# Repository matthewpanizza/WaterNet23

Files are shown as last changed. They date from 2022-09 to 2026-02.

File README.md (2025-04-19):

# WaterNet23 - Autonomous Water Vehicles
Repository for WaterNet23 Code and Schematics

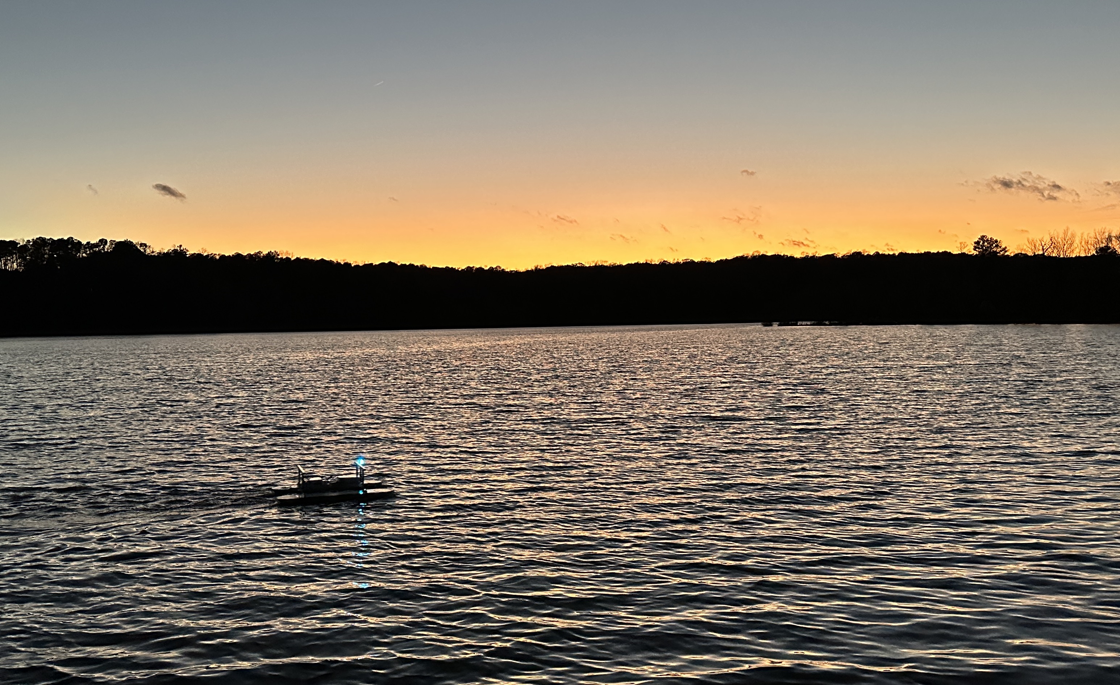
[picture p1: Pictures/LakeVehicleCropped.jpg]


## Background

This project was started as part of the one-year NC State ECE Senior Design class in January 2022. The goal of this project was to develop a series of low-cost autonomous water surface vehicles which could collect water quality measurements of aquaculture ponds. This README contains information on how to set up the water vehicles for operation and details on the hardware and software used for the project.

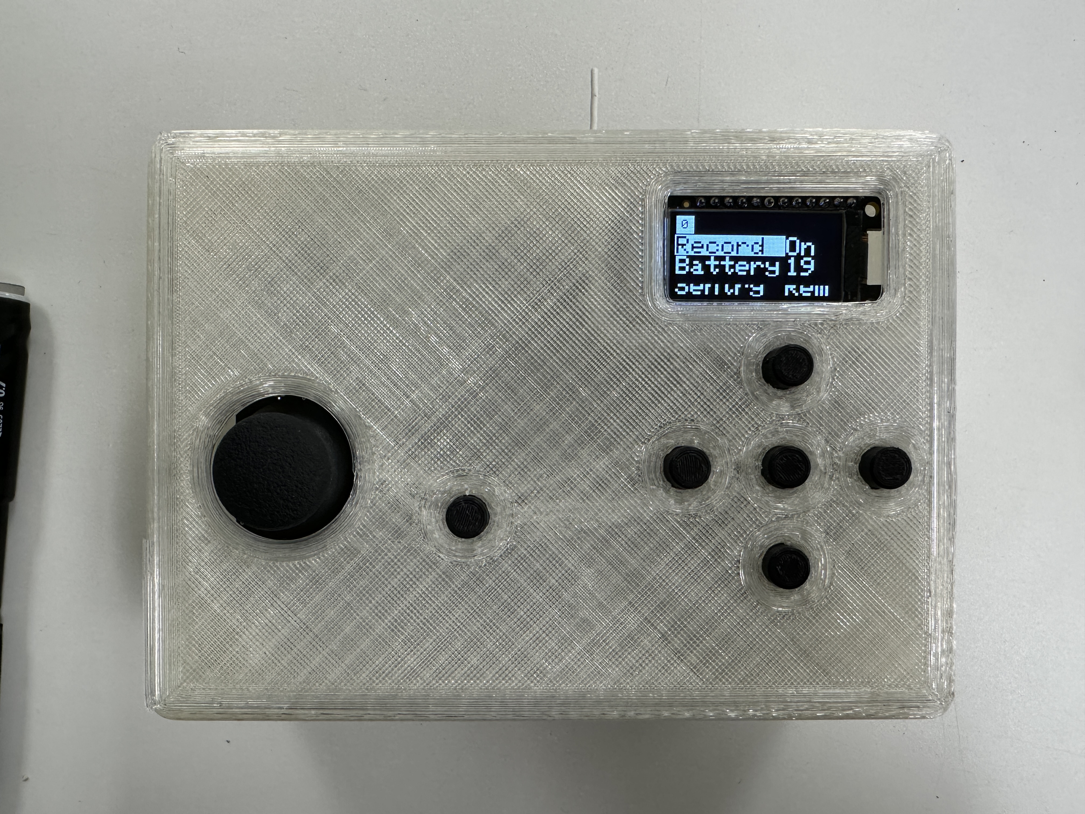
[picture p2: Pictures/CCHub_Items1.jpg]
 

This project has two parts - the water vehicles and the Central Control Hub (CCHub). The CCHub communicates wirelessly with the vehicles using XBee (900MHz), Cellular (LTE) and Bluetooth Low Energy (BLE) with support for up to 10 vehicles. The water vehicles report telemetry back to the CCHub, which is then displayed on the CCHub's screen. The vehicles have three operation modes for movement: remote control, sentry and autonomous. Remote control allows for control using the CCHub joystick. Sentry mode captures the current GPS location and attempts to keep the vehicle within a set radius of that point. Autonomous mode allows for navigation to GPS waypoints which are fed into the CCHub over Serial from a companion computer. See the [Operating the Water Vehicles](#operating-the-water-vehicles) section for more information on how these functions work.

## Table of Contents
 - **[Features](#features)**: Hardware/software capabilities of the vehicles and CCHub.
 - **[Operating the Water Vehicles](#operating-the-water-vehicles)**: How to use the CCHub to control the water vehicles.
 - **[Hardware](#hardware)**: Information about the hardware components used on the CCHub and vehicles.
 - **[Software](#software)**: Information about the software communication and control systems.
 - **[Setting Up the Development Environment](#setting-up-the-development-environment)**: Information about hwo to install Visual Studio Code and upload code to the microcontrollers.
 - **[Software Architecture](#software-architecture)**: Information about common software practices used in the programming of the boards and quick links to get you started on understanding the microcontroller functions.

## Features
 - Network support for controlling up to 10 water vehicles
 - Autonomous navigation mode for movement to GPS waypoints
 - Sentry mode to maintain position for continuous measuring in one place
 - Graphical menu for configuring vehicles and observing status
 - Redundant communication via LTE, XBee and Bluetooth LE
 - Water quality sensing for temperature, dissolved oxygen, pH, and conductivity
 - Logging of water quality measurements on a micro-SD card
 - Wireless copying of water quality measurements from vehicles to CCHub micro-SD card
 - 80W solar panel for long-term stationary monitoring
 - Light tower for observing vehicle status from shoreline
 - Leak detection emergency shutoff

## Operating the Water Vehicles

This section has instructions for powering up the water vehicles and operating them using the Central Control Hub.

### Powering the CCHub and Water Vehicles

The CCHub has a micro USB port on its side which needs to be powered with a high-amperage (2.1A) USB brick or power bank. Once plugged in, the CCHub will automatically attempt to establish Cellular connection and receive messages from the water vehicles.

The water vehicles are powered from the a Lithium-ion battery pack and have a button for powering up the board. There is a latching mechanism on the main board which will keep the power on once the microcontroller has started operating. Hold the power button for five seconds to ensure the power latch is enabled. Like the CCHub, the water vehicles will attempt to establish a Cellular connection and will broadcast periodic messages for the CCHub to pick up.

Once a vehicle has connected to cellular and the CCHub has received the message, it will show up on the CCHub screen as a block with its identifier ID. See the next section for how to navigate the menu on the CCHub.

### Menu Navigation

The CCHub menu is navigated using the integrated DPAD buttons. When not modifying a setting, the left/right buttons switch which vehicle is being controlled, and the up/down arrows navigate which item is being selected. To modify one of the settings, press the enter button and it will highlight the value to be changed. Use the left/right buttons to modify the value and press enter to confirm. There is also an emergency stop toggle next to the joystick which will stop motion of all vehicles.

#### Settings
- **Record**: Enables/Disables logging of water quality measurements to the SD card (on/off)
- **Battery**: Estimated battery percentage of the water vehicle's battery (not editable)
- **Sentry**: The current [Driving Mode](#driving-modes) of this water vehicle (Rem/Sen/Aut)
- **Signal**: Turning on signal causes the light tower of this vehicle to flash amber (on/off)
- **SolPwr**: Shows how many watts the solar panel is generating (not editable)
- **BatPwr**: Shows how many watts are being drawn from the Lithium-ion battery (not editable)
- **Offload**: Starts a copy of all files from the vehicles microSD card to the CCHub microSD card over Bluetooth. Only enable when vehicles are docked! (on/off)

### Driving Modes

#### Remote Control (Rem)

Remote control mode allows the user to use the joystick on the CCHub to control the direction and speed of the vehicle manually like an RC car. In remote mode, the joystick controls whichever vehicle is currently selected on the menu.

#### Sentry (Sen)

Changing the control mode to Sentry mode will send a target latitude and longitude waypoint to the vehicle and have the vehicle navigate to that point. After it reaches that point, it will use the GPS and compass to navigate back to that target point if it goes farther than a set radius (current software is set to 4 meters). This mode can be used to take samples of one part of a water body over a large period of time, as it will correct for water currents pushing the vehicle.

#### Autonomous (Aut)

Changing the control mode to autonomous mode will send a target latitude and longitude waypoint to the vehicle and have the vehicle navigate to that point. These GPS waypoints are fed into the CCHub via the USB port which is connected to companion computer. See the next section for information about the companion computer.

### Companion Computer and Waypoints

The CCHub is set up to be connected over USB to a companion computer such as a Raspberry Pi for automated sending of GPS waypoints. There are a series of commands that can be sent to the CCHub which are then transmitted to the water vehicles. See the [Companion Computer to CCHub Command Structure](#companion-computer-to-cchub-command-structure) section for how to send the GPS waypoints to the CCHub.

### Light Tower Statuses

The water vehicles are equipped with a small light tower that has an RGB LED. The LED will change colors/blinking patterns depending on which mode it is in and which communication protocols are available.

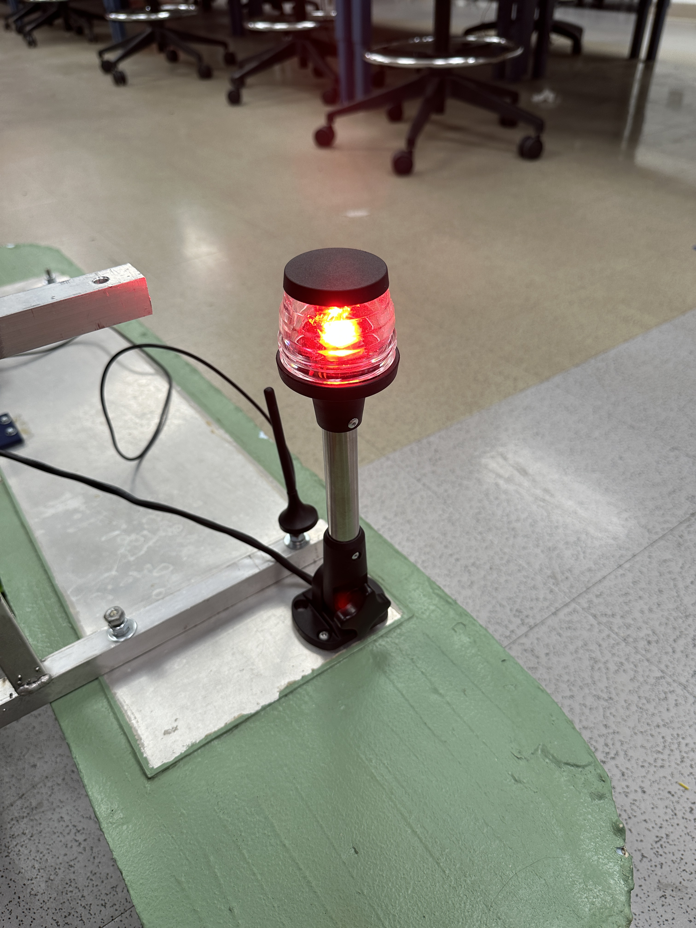
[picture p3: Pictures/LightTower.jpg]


#### Color Schemes
Color     | Description
----------|------------------------------------------
CYAN      | All modes of communication are available
YELLOW    | XBee and BLE are available
WHITE     | LTE and BLE are available
BLUE      | Only BLE available
GREEN     | XBee and LTE available (typical when out in water)
ORANGE    | Only Xbee available
MAGENTA   | Only LTE is available (recovery mode)
RED       | No communication available

#### Blinking Patterns
Pattern            | Description
-------------------|---------------------------
Blinking (normal)  | Battery is low
Blinking (slow)    | Sentry Mode
Fading             | Autonomous Mode
Solid              | Manual Mode

#### Special Modes
Pattern               | Description
----------------------|----------------------------------
Fast Blinking Blue    | Copying micro-SD data to CCHub
Fast Blinking Amber   | Signaling response from CCHub

### Water Quality Sensors
The water vehicles are equipeed with a series of water quality sensors which connect to five SMA connectors on the side of the enclosure. Ensure the sensors are color-matched to the daughter boards on the vehicle PCB. See the [Atlas Scientific Water Quality Sensors](#atlas-scientific-water-quality-sensors) section for how these sensors work and how to configure them on new vehicles.

### Micro-SD Card Logging
Each of the water vehicles have an onboard Micro-SD card reader (on underside of PCB) which is used to store the water quality measurement in a CSV file. This file can be opened in Excel or other sheet processing programs for data analysis of the collected measurements. Below are a few sample measurements on a bench for the temperature and pH probes.

Time           | Latitude | Longitude | Temperature | pH       | Dissolved O2 | Conductivity 0.1K | Conductivity 1K
---------------|----------|-----------|-------------|----------|--------------|-------------------|-----------------
08132022201055 | 0.000000 | 0.000000  | 32.425999   | 3.623000 | 0.000000     | 0.000000          | 0.000000
08132022201057 | 0.000000 | 0.000000  | 32.437000   | 3.616000 | 0.000000     | 0.000000          | 0.000000
08132022201100 | 0.000000 | 0.000000  | 32.438999   | 3.604000 | 0.000000     | 0.000000          | 0.000000
08132022201102 | 0.000000 | 0.000000  | 32.443001   | 3.614000 | 0.000000     | 0.000000          | 0.000000

## Hardware

### Water Vehicle PCB



### Water Vehicle Block Diagram

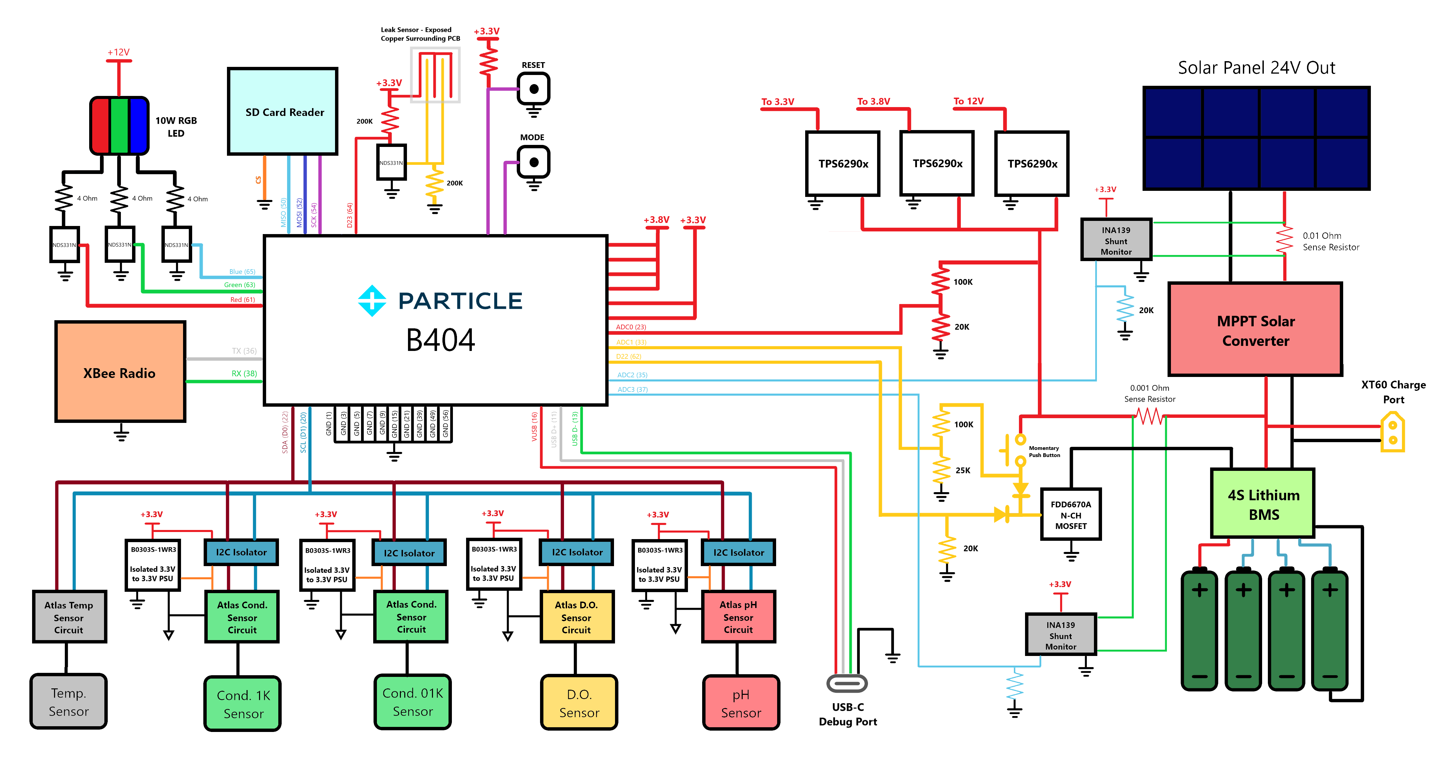
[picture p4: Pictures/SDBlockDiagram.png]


### Particle B402/B404X Microcontroller



For controlling all of the hardware on both the vehicles and CCHub, we used the Particle B-Series System-on-a-Module (BSoM). We chose the BSoMs for their integrated Cellular and Bluetooth Low-Energy communication capability and relatively low cost (~$55/module). These microcontrollers have fairly generous IO and memory capability and are easy to program in C++ using their Particle DeviceOS hardware abstraction layer (HAL). Particle also includes 100MB/month of cellular data in their free plan, which would be plenty for using LTE as a fallback communication mechanism. See the [Software Architecture](#software-architecture) section for more details on how to set up the environment for developing and uploading the firmware on the BSoM.

### Atlas Scientific Water Quality Sensors

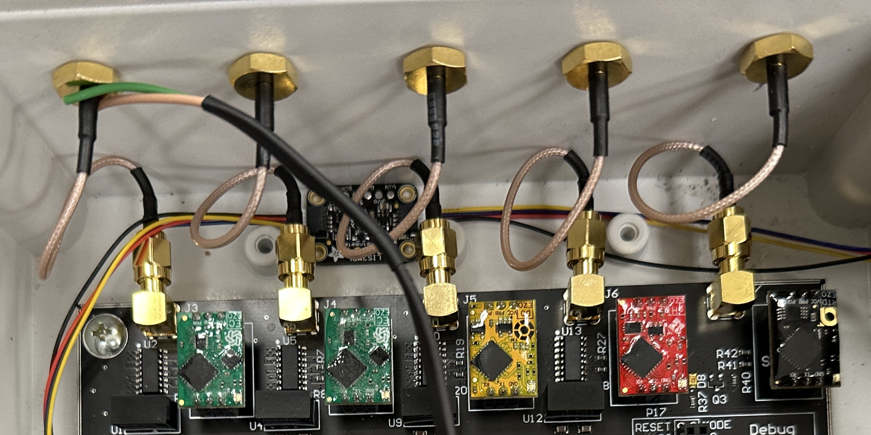
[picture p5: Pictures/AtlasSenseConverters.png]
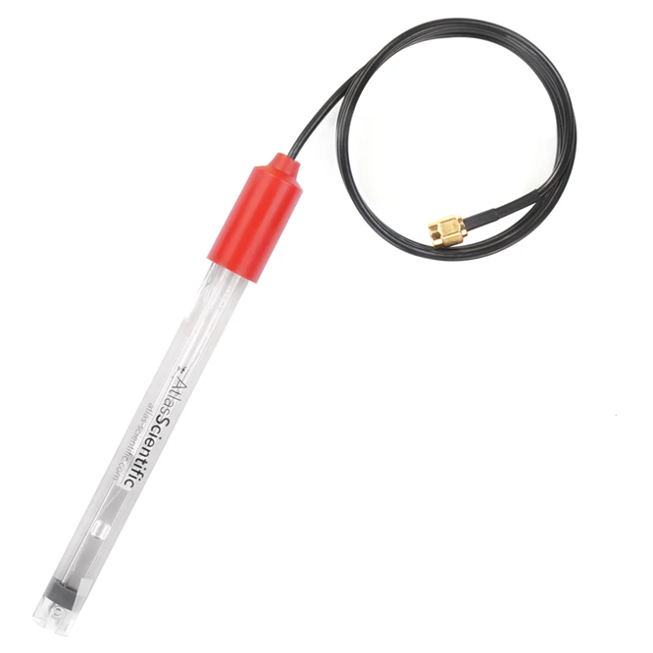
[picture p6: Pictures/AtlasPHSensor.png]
 

The water vehicles have a series of [Atlas Scientific](https://atlas-scientific.com/) water quality sensors. The sensor probes connect using a set of SMA connectors which mount to the exterior of the main PCB enclosure. Ensure the sensors are connected to the SMA connector that matches the circuit (red pH probe goes to the connector in front of the red EZO module). Currently, the vehicle is equipped with the following sensors:

- [Temperature](https://atlas-scientific.com/probes/standard-temp-probe/)
- [pH](https://atlas-scientific.com/probes/consumer-grade-ph-probe/)
- [Dissolved Oxygen](https://atlas-scientific.com/probes/dissolved-oxygen-probe/)
- [Conductivity K 0.1](https://atlas-scientific.com/kits/conductivity-k-0-1-kit/)
- [Conductivity K 1.0](https://atlas-scientific.com/kits/mini-conductivity-k-1-0-kit/)

These sensors use their standard [EZO](https://atlas-scientific.com/embedded-solutions/ezo-ph-circuit/) interface which communicates over I2C to the BSoM microcontroller. Since the interface is standard, the modules/sensors can be swapped out for others that Atlas sells such as the [Oxygen reduction potential](https://atlas-scientific.com/orp) sensor with some slight code modifications.

#### Important Note
The sensors need to be configured to operate in I2C mode with a particular address. By default, they operate in UART mode. See the [pH EZO datasheet](https://files.atlas-scientific.com/pH_EZO_Datasheet.pdf) for the commands needed to switch to I2C mode. You can communicate over UART using a simple USB COM Port adapter (such as FT232RL) or using an Analog Discovery 2. In the software, there are macros which set the I2C address used by each sensor:

```cpp
#define PHADDR              99              //default I2C ID number for EZO pH Circuit.
#define MCOND               100             //default I2C ID number for EZO Mini-Conductivity (0.1)
#define COND                101             //default I2C ID number for EZO Conductivity Circuit. (1.0)
#define TEMPADDR            102             //Default I2C address for temperature sensor
#define DOADDR              97              //Default I2C address for Dissolved Oxygen sensor
```

The I2C system also has a set of I2C isolator circuits which are necessary to prevent interference between the sensors when they make contact with water. Without the isolators, the sensors will feed back into each other and cause inaccurate readings. All EZO circuits, except the temperature probe, have the I2C isolation. The isolation is done using a 3.3V to 3.3V isolated power supply and a I2C isolator IC.

### XBee Radio

In addition to Cellular and BLE, we included a XBee S3B wireless module on the vehicles and CCHub. These modules offer greater range (up to 9 miles!) at similar latency to BLE. The XBee modules we chose operate in the 900MHz range (the same as LoRa), and offer an easy-to-use mesh based communication between all modules in the network. These modules essentially act as a wireless UART console between all nodes in the network, and our command structure handles negotiation of the destination node. Below is an example of communication with XBee between two microcontrollers:

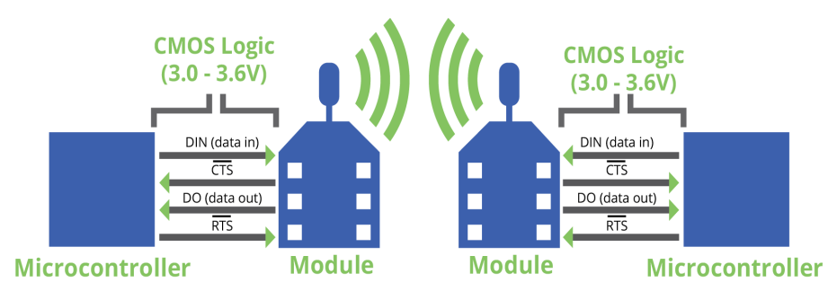
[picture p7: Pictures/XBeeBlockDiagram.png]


**Important Note**: The XBee modules require network setup to become part of a mesh network. Check out this [Instructables setup guide](https://www.instructables.com/How-to-Use-XBee-Modules-As-Transmitter-Receiver-Ar/) for configuring them. For setting up new vehicles, connect the XBee from the CCHub to XCTU and get the channel number. For more information about the XBee S3B Modules, check out the [Datasheet](https://docs.digi.com/resources/documentation/digidocs/pdfs/90002173.pdf).

### Neo-M8U GPS

For autonomous navigation, we decided to use the [Neo-M8U GPS](https://www.sparkfun.com/sparkfun-gps-dead-reckoning-breakout-neo-m8u-qwiic.html) for its accuracy at low cost. This module also has the convenience of the [QWIIC](https://www.sparkfun.com/qwiic) interface for powering and communicating with it. 

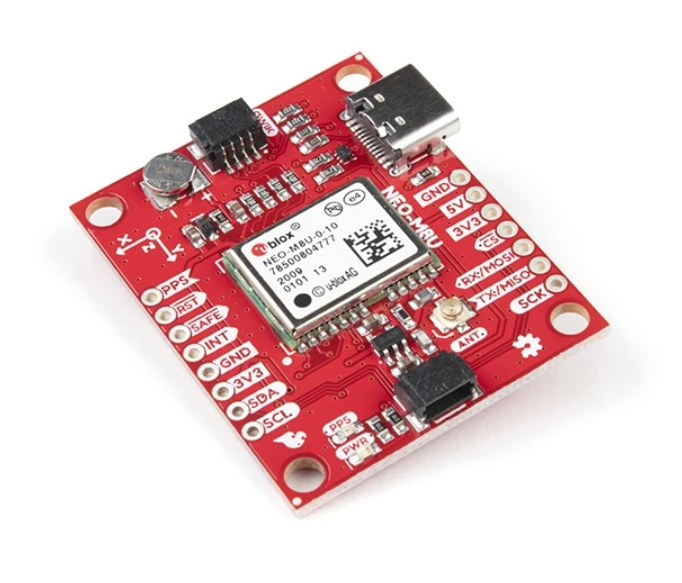
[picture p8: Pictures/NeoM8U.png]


We initially wanted to use its untethered dead reckoning (UDR) feature to enable better accuracy and make use of its internal IMU for getting the water vehicle's heading and speed, however getting this feature proved difficult for our timeline. The UDR feature unfortunately requires some calibration at higher speeds than our water vehicle supports, so we only ended up using it for it's GPS position data. Interfacing with the GPS module was done using the [SparkFun Ublox Arduino Library](https://github.com/sparkfun/SparkFun_Ublox_Arduino_Library).

### LIS3MDL Compass

With the untethered dead reckoning feature not working, the Neo-M8U GPS was not able to provide a heading, we decided to add a [LIS3MDL compass](https://www.adafruit.com/product/4479) as a substitute. At this point, we had about a month remaining in the project and had to find a quick solution. The compass conveniently used the QWIIC interface so it was easy to install.

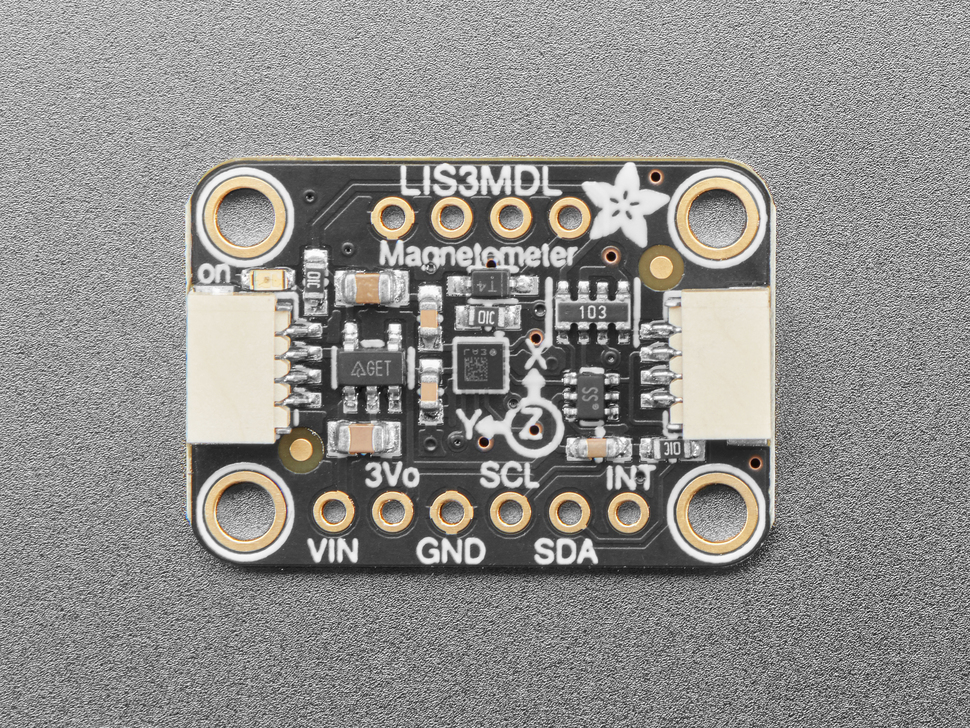
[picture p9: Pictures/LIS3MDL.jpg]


On the lab bench, this compass proved to do the trick, but we quickly realized (with no time left in the project) that any tilt of the module (a frequent occurrence on water!) will wildly throw off the readings. This bad reading caused our autonomous movement algorithm to perform circles. To overcome this, we could use a tilt-compensated module such as the GY-511 which has an accelerometer.

### Motor Drive System

For a movement system, we wanted to upgrade the basic paddle-style rotors to some off-shelf turbine-style motors for their improved efficiency and higher speed capability. We paired the brushless motor turbines with some off-shelf Electronic Speed Controllers (ESCs), which take a simple [duty-cycle based 50Hz PWM signal](https://howtomechatronics.com/tutorials/arduino/arduino-brushless-motor-control-tutorial-esc-bldc/) for control. These motors got mounted on the inside of both styrofoam blocks and allow for tank-style movement.

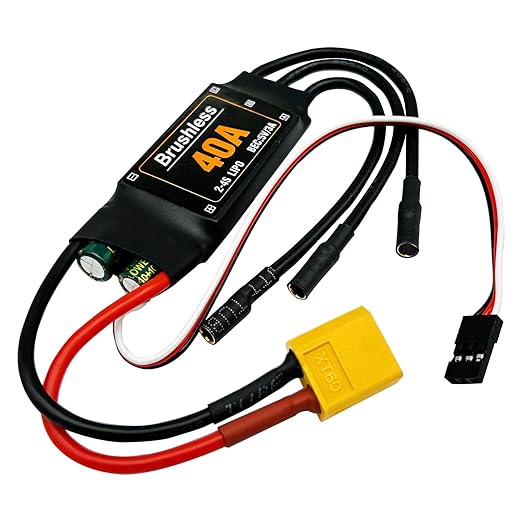
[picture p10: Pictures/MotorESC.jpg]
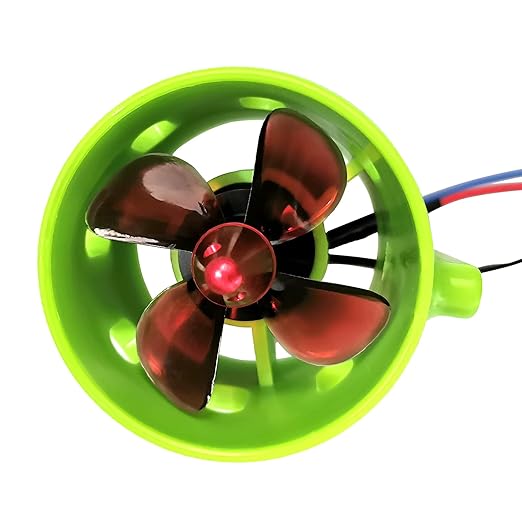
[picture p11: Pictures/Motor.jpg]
 

### Light Tower LED Driver

The vehicle PCB has an LED driver for a common-anode 12V RGB LED. This LED is wired through a light tower to the four pin connector on the PCB. Below is an example of the RGB LED that can be used for the light tower.

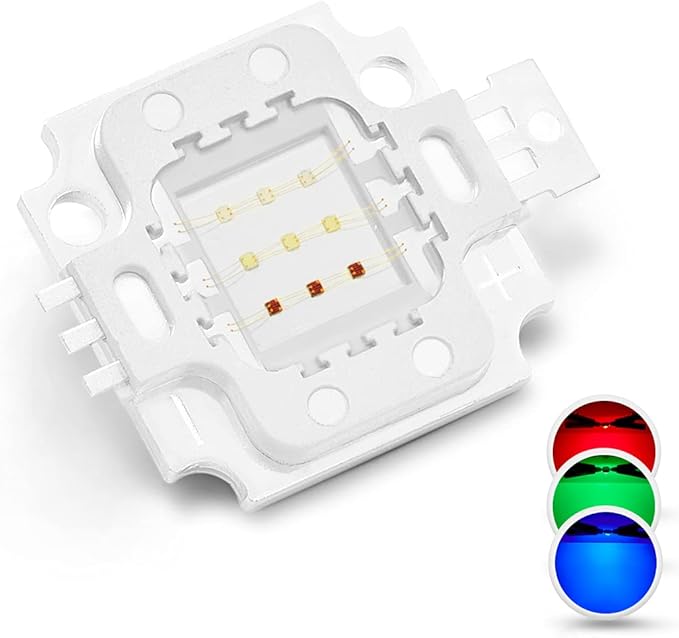
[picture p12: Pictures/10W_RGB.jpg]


### Water Vehicle Power System

One of the intentions of these water vehicles was to have them  monitor one place on an aquaculture pond for many days on end. To achieve this, we both needed a large battery and a solar charging system. The battery was constructed out of [21700 Lithium-ion](https://liionwholesale.com/collections/batteries/products/lishen-21700-lr2170sd-9-6a-flat-top-5000mah-battery-genuine) cells and had a 4-series (14.8V nominal), 6-parallel configuration which gave it a capacity of ~450 watt-hours. The battery was constructed using a spot welder and had an off-shelf 4S Battery Management System (BMS) for regulating charging/discharging.

We also equipped it with a 80W solar panel to have the battery recharge during the day.



For solar charging, we purchased a Maximum-power-point-tracker PCB for handling battery charging from the solar panel. This PCB regulates the amount of power being drawn from the solar panel to ensure the maximum wattage is generated for the given lighting conditions.

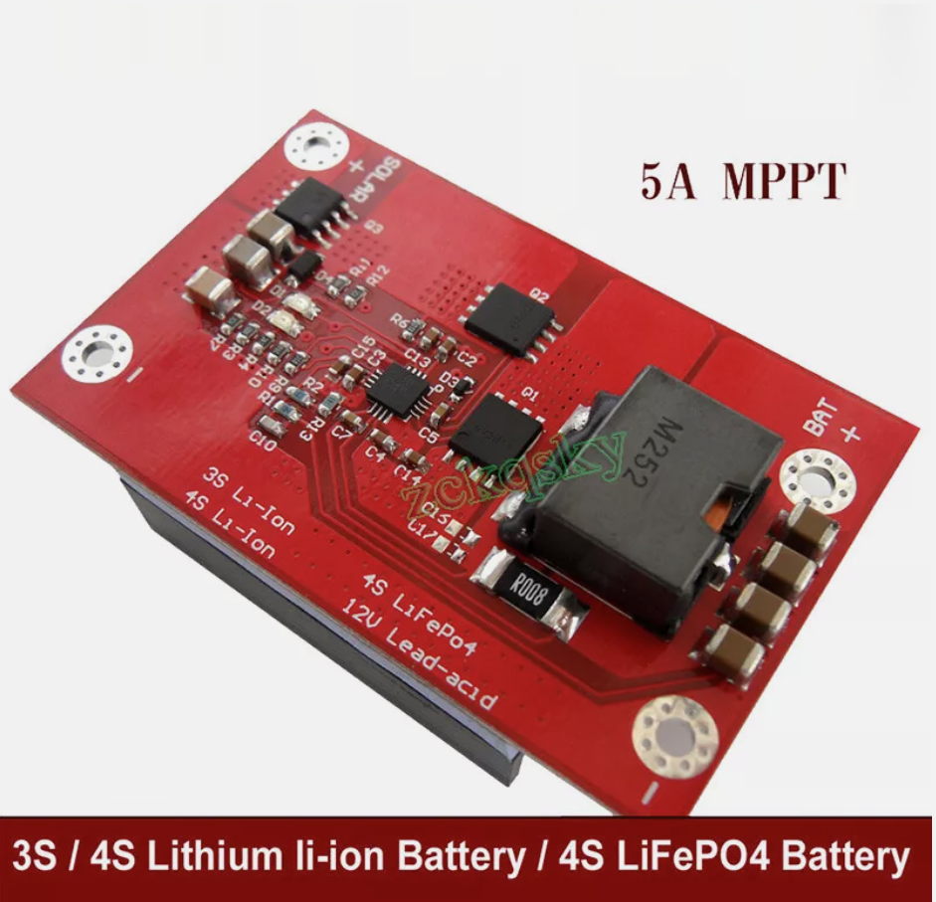
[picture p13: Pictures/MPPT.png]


Integrated in the water vehicle PCB are two XT-30 power ports, one for the MPPT output and one for the battery. These ports also have a [Shunt Monitor](https://learn.sparkfun.com/tutorials/ina169-breakout-board-hookup-guide/all) for measuring the amount of power being drawn by each of the two power sources.

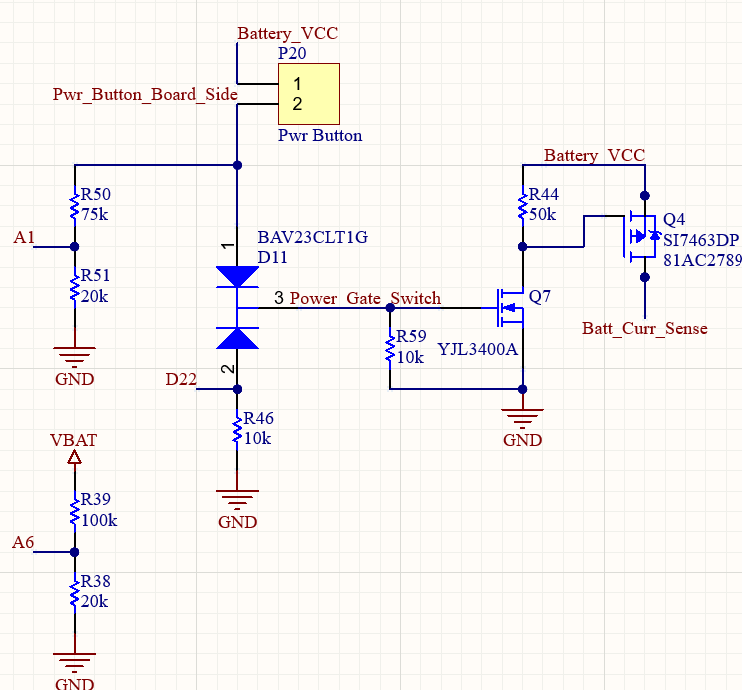
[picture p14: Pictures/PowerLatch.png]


The power system also has a special latch mechanism for powering up and maintaining power on the vehicle PCB. The latch is first enabled by the user holding down the power button, and is then held on by the BSoM until it is ready to be turned off. There is a leak-detection trace that runs around the outside of the vehicle PCB which sends a singal to the BSoM when water is detected. The BSoM can then turn off the latch as an emergency shutoff to prevent corrosion due to water damage.

### Central Control Hub Dev Board

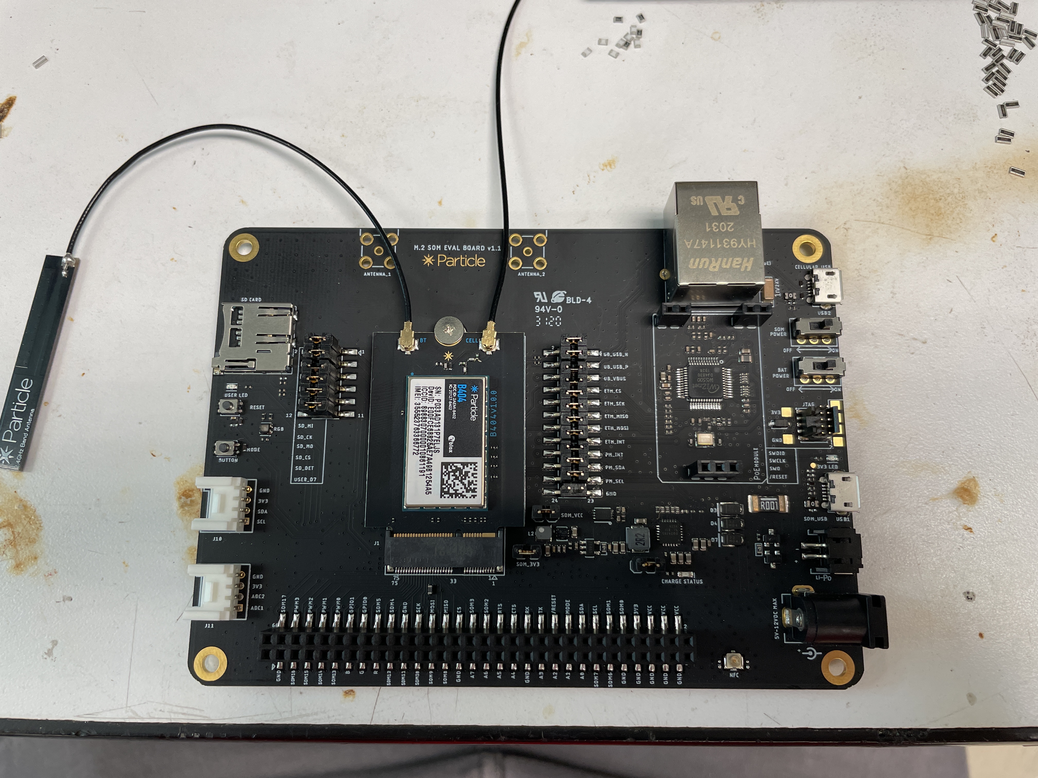
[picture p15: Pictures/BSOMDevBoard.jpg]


### Central Control Hub Block Diagram

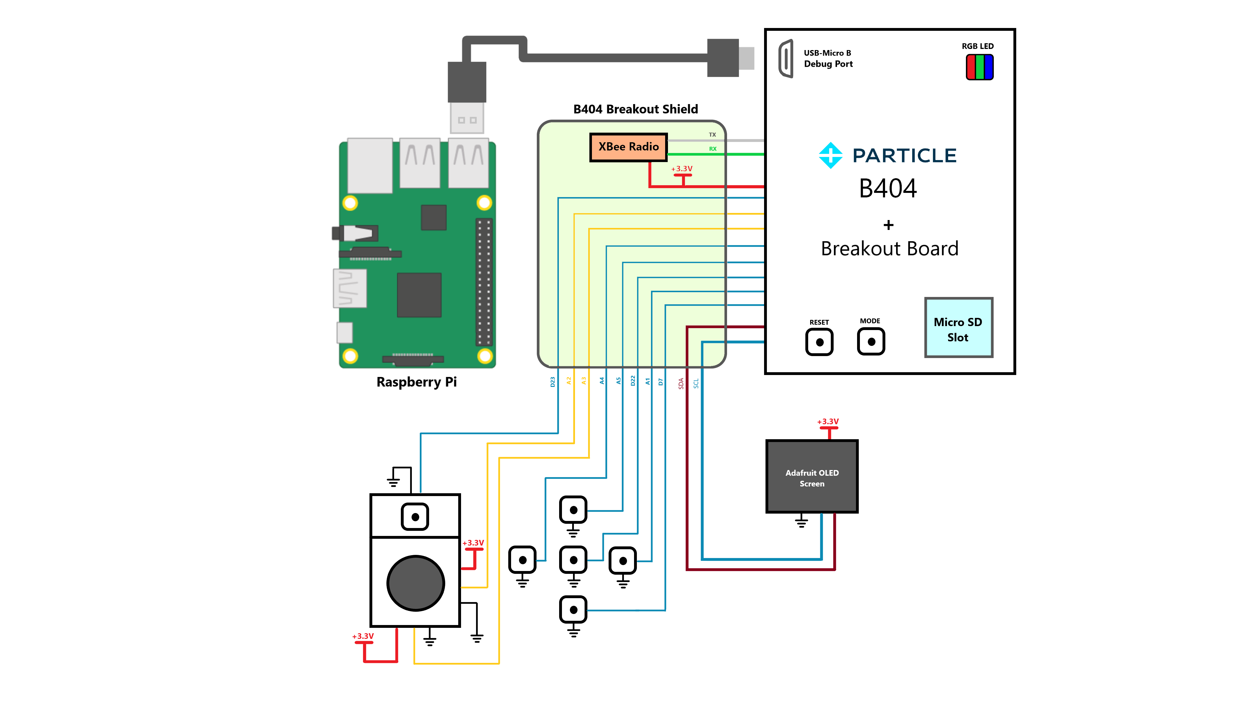
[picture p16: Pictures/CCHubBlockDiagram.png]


This block diagram shows the button configuration of the CCHub's daughter board. The daughter board acts like a Raspberry Pi's Hat and connects to the multi-pin header on the BSoM dev board.

### Central Control Hub Screen

To display the user interface on the CCHub, we included a [SH1107-based OLED Screen](https://www.adafruit.com/product/4650) from Adafruit. It is 128x64 pixels and allows us to display three menu items at a time and the bot selection tabs. This attaches to the daughter board of the CCHub and communicates over I2C to the BSoM.

## Software

This section contains information about software components and configuration settings

### Water Vehicle Identifier

The water vehicle software has a macro which is used to uniquely identify each vehicle in the network. This macro is located at the top of the WaterNet23Vehicle.ino file and is called `BOTNUM`. Change this number to something between 0 and 9 and ensure these numbers are unique across the bots in your network or clashing of commands will occur.

**TODO**: Compile a unique identifier based on the serial number of the BSoM

### Redundant Communication System

The water vehicles are designed with three communication modes: Bluetooth Low-Energy, XBee, and Cellular. This was to allow for a balance of range, latency, and reliability between the vehicles and CCHub. The communication system uses the same command structure (see the [Command Structure](#cchub-to-vehicle-command-structure) section) across all modes of communication, but prioritizes communication in the following order: XBee, BLE, then Cellular.

### Basic Autonomous Navigation Algorithm

For autonomous movement, we set up a GPS waypoint system where the target latitude and longitude were relayed from the CCHub to the water vehicles. The vehicle would then calculate the target heading, relative to north, of its current latitude and longitude (X2). Then, using the compass heading, it would calculate the heading delta (X1 + X2), which would range from -180 to +180. This could then be mapped to the motor speeds on the left and right side. Positive values of heading delta would speed up the left motor and negative values would speed up the right motor. For the few tests where the compass calibration was accurate (see the [compass section](#lis3mdl-compass) for more details), this correctly had the vehicle turn around and head toward a point.

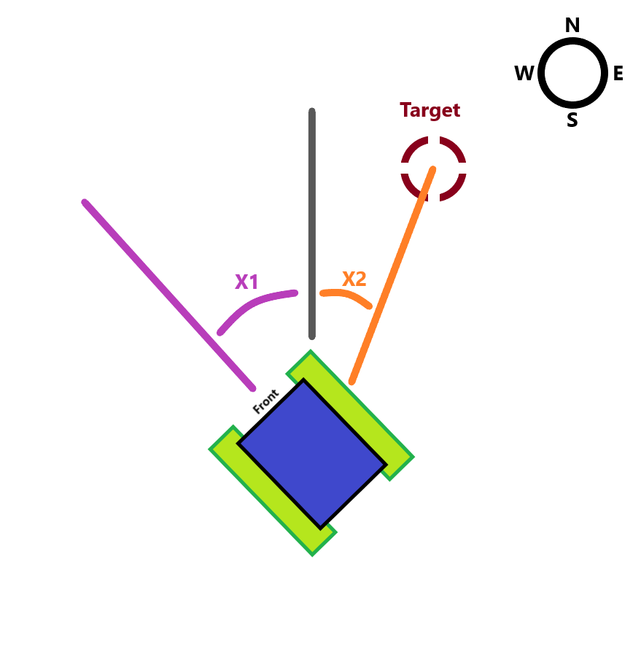
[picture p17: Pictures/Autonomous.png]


### CCHub to Vehicle Command Structure

This section has information about the commands exchanged between the CCHub and water vehicles. These commands are processed in the `processCommand()` function in the code and have the following structure:

```
XXYYCCCAAAAAAAAAAAAZZ (Max 255 bytes)

XX:  Source controller (CC = CCHub, Bx = Bot number x)
YY:  Target controller(s) (Bx = bot number x, AB = all bots)
AA+: Data payload associated with command
CCC: 3-byte command type
ZZ:  Checksum for the command string. Total number of bytes in the string.
```

#### Commands to Vehicle

- `ctl` -  Control Command

Main command for updating the state of the water vehicle. Takes a space-separated payload with the following information:
```
U V W X Y Z

U = Target Latitude (float)
V = Target Longitude (float)
W = Drive Mode (integer, 0 = manual, 1 = sentry, 2 = autonomous)
Y = Sensor Logging Enabled (0 = disabled, 1 = enabled)
Z = LED Signaling Enabled (0 = disabled, 1 = enabled)
```

- `mtr` -  Motor Speed Command

Takes a 3-character speed for each motor. 0 represents full speed in reverse, 180 represents full speed forward.
```
XXXYYY

XXX = Left Motor Speed (0-180)
YYY = Right Motor Speed (0-180)
```

- `req` - Data Request Command

Takes no arguments. Requests that the water vehicle send a sample of each water quality measurement back to the CCHub

- `pts` - Put-String Command

Debug command that takes any characters in the payload and writes them to the log file on the SD card and prints it out to the USB serial console.

- `spc` - Status Check Command

Takes no arguments. A simple message which allows the vehicle to determine if the CCHub has communication with it.

- `hwa` - Hello World Acknowledge Command

Takes no arguments. Hello World! This message is sent by the CCHub periodically while waiting for bots to be paired. The bots can have a flag set to prevent any actions on startup until this command is received.

- `dmp` - SD Card Dump Command

Takes no arguments. Causes the vehicle to enter [Offload Mode](#setting-up-the-development-environment) where all data from the microSD card is copied over Bluetooth LE to the CCHub. Depending on the size of the data, this can take a long time. Only execute this command when at shore as motor control is not active during this mode!

- `egp` - Emulated GPS Point Command

Updates the GPS point normally set by the Control Command for doing benchtop testing. Takes a space-separated payload with the following information:

```
U V

U = Target Latitude (float)
V = Target Longitude (float)
```

- `stp` -  Emergency Stop Command

Takes no arguments. Sets both motors to idle.

#### Responses from Vehicle

- `sup` - Status Update Command

Main command sent by the vehicle which updates the items in the CCHub menu. Takes a space-separated payload with the following information:
```
U V W X Y Z

U = Battery percentage (integer, 0-100%)
V = Status flags (16-bit integer bitmask)
W = Current latitude (float)
X = Current longitude (float)
Y = Battery power (integer, watts)
Z = Solar panel power (integer, watts)
```

- `sns` - Sensor Reading Command

Command with the most recent reading of all sensors on the water vehicle. Takes a space-separated payload with the following information:
```
T U V W X Y Z

T = Current latitude (float)
U = Current longitude (float)
V = Dissolved oxygen (integer, multiplied by 1000)
W = pH (integer, multiplied by 1000)
X = Conductivity (integer, multiplied by 1000)
Y = Mini Conductivity (integer, multiplied by 1000)
Z = Temperature (integer, multiplied by 1000) (integer, watts)
```

- `hwd` - Hello World Command

Takes no arguments. This is sent periodically by the water vehicle when it has not received any messages from the CCHub yet. The CCHub will reply to this message with the Hello World Acknowledge command.

- `pts` - Put-String Command

Debug command that takes any characters in the payload and writes them to the log file on the SD card and prints it out to the USB serial console.

- `ldt` - Leak Detected Shutoff Command

Takes no arguments. Signals that a leak has been detected on the main vehicle PCB and that the microcontroller has executed an emergency shutoff.

- `ldb` - Leak Detected Battery Shutoff Command

Takes no arguments. Signals that a leak has been detected in the battery enclosure and that the microcontroller has executed an emergency shutoff.

- `wld` - Leak Detected Warning Command

Takes no arguments. Signals that a leak has been detected on the main vehicle PCB. The microcontroller has not shut off the power.

- `wld` - Leak Detected Battery Warning Command

Takes no arguments. Signals that a leak has been detected in the battery enclosure . The microcontroller has not shut off the power.

### Companion Computer to CCHub Command Structure

This section has information about the commands exchanged between the CCHub and Raspberry Pi companion computer. These commands are processed in the `processRPiCommand()` function in the code and have the following structure:

```
XXYYCCCAAAAAAAAAAAAZZ (Max 255 bytes)

XX:  Source controller (RP = Raspberry Pi, CC = CCHub)
YY:  Target controller(s) (RP = Raspberry Pi, CC = CCHub)
AA+: Data payload associated with command
CCC: 3-byte command type
ZZ:  Checksum for the command string. Total number of bytes in the string.
```

#### Commands to CCHub

- `ctl` - Water Bot Control Command

Main command sent by the RPi which updates the items in the CCHub menu. Takes a space-separated payload with the following information:
```
T U V W X Y Z

T = The water vehicle ID this command is targeted at (integer)
U = Target latitude (float)
V = Target longitude (float)
W = Drive Mode (integer, 0 = manual, 1 = sentry, 2 = autonomous)
X = Offloading mode (integer, 0 = disabled, 1 = enabled)
Y = Sensor recording enabled (integer, 0 = disabled, 1 = enabled)
Z = Signaling mode enabled (integer, 0 = disabled, 1 = enabled)
```

Example: `RPCCctl1 35.764730 -78.680762 2 0 1 0`

Configures vehicle 1 to enter autonomous mode and move to GPS location 35.764730 -78.680762 with sensor recording enabled.

#### Responses from CCHub

- `sup` - Status Update Command

Main command sent by the CCHub to update the water vehicle status to the RPi.Takes a space-separated payload with the following information:
```
T U V W X Y Z

T = Water vehicle number
U = Water vehicle battery percentage
V = Current latitude (float)
W = Current longitude (float)
X = Status flags (16-bit integer bitmask)
Y = Battery power (integer, watts)
Z = Solar panel power (integer, watts)
```

## Setting Up the Development Environment 

This section will explain how to install Visual Studio Code and set up the Particle workbench for installing and creating firmware on the microcontrollers.

### Software Requirements
- [Visual Studio Code](https://code.visualstudio.com/): Main development environment for writing code and flashing firmware to devices.
- [Particle Workbench](https://marketplace.visualstudio.com/items?itemName=particle.particle-vscode-pack) extension for Visual Studio Code to support flashing of Particle devices.
- [Git for Windows](https://git-scm.com/downloads/win): Optional for interaction with Git repositories. Get this if you will be making changes to the software/hardware and need to track changes.
- [Tortoise Git](https://tortoisegit.org/download/): Optional graphical tool for performing repository actions. Get this if you will be making changes to the software/hardware and need to track changes.
- [Optional] Serial Console (I prefer the one in the [Arduino IDE](https://www.arduino.cc/en/software))

### Cloning a Repository

To get a copy of the code repository for one of the projects, you'll need to clone down the repo. I prefer to use TortoiseGit, but other Git interfaces will also work. Find a folder where you want to have the repo downloaded, right click, and choose ToritoiseGit -> Git Clone (Windows 11 may need to click "show more options").

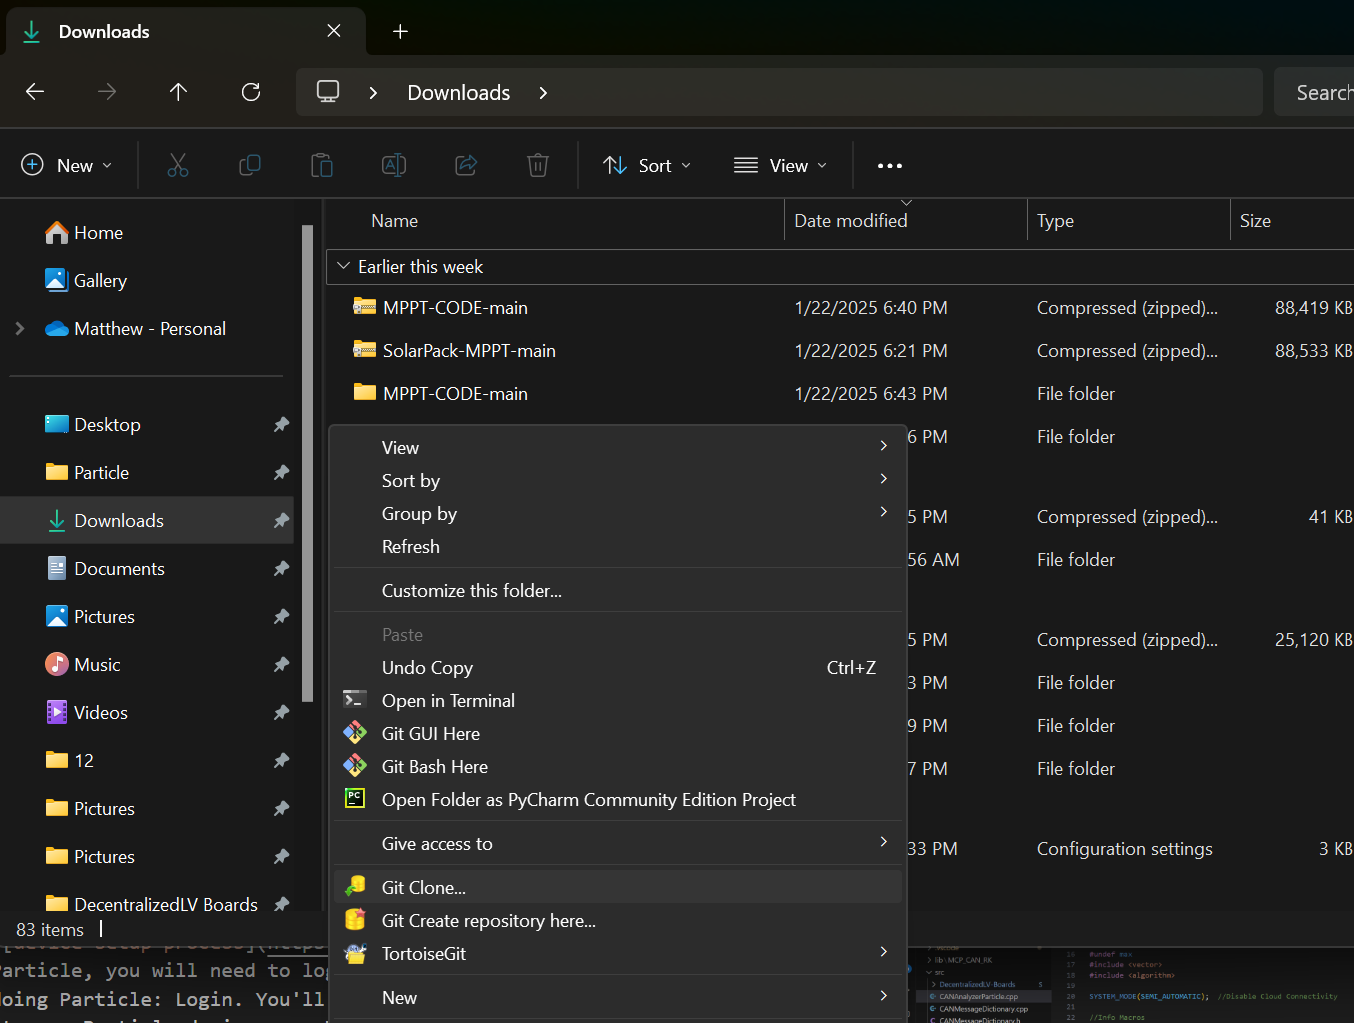
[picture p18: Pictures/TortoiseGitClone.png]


In the menu that pops up, you'll need to enter a source for where the repo is located. You can find this on GitHub by expanding the "Code" menu. If you are planning on making changes to the code, it is recommended that you make a new branch on GitHub such that the working code is maintained on the `master` or `main` branch.

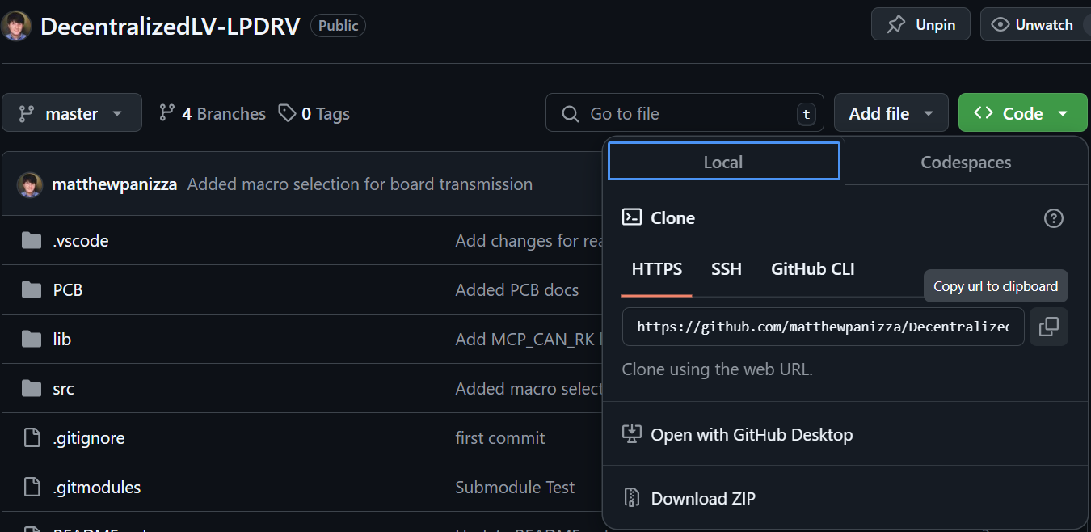
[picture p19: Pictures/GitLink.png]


Once you've gotten a link and made a new branch, paste the link in the Tortoise menu and enter the branch you wish to clone down.

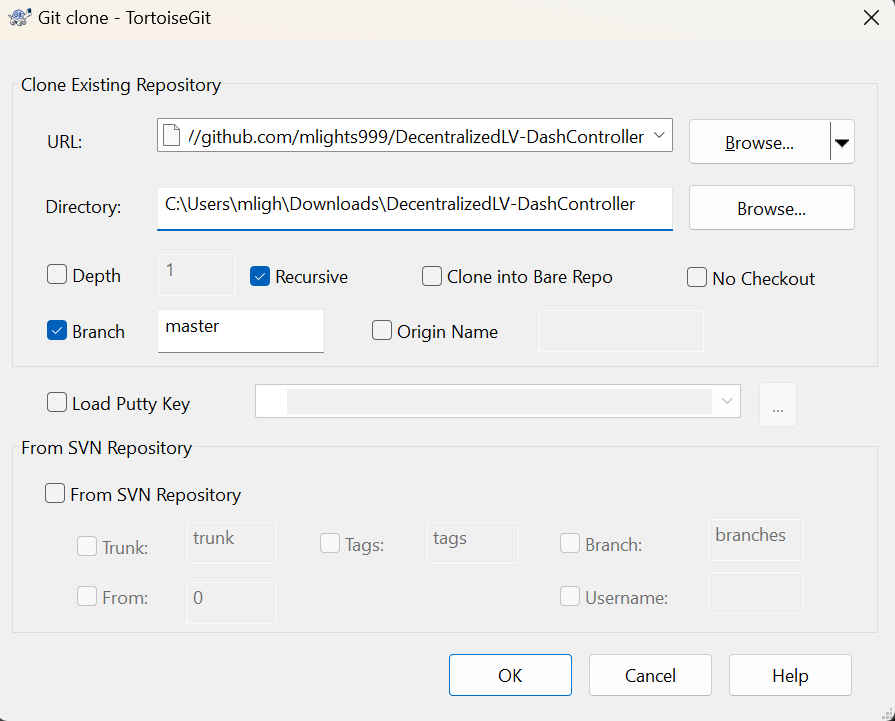
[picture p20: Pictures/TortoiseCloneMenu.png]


Press OK, and TortoiseGit should begin cloning down the repo. You may be asked to sign in to your browser on first setup.

### Opening Project and Flashing Firmware

After installing Visual Studio Code and the Particle Workbench Extension, you're now ready to install the firmware on the microcontroller. First, open up the cloned repository of the Particle project in Visual Studio Code by going to the Particle tab on the left toolbar and choosing Open Folder.

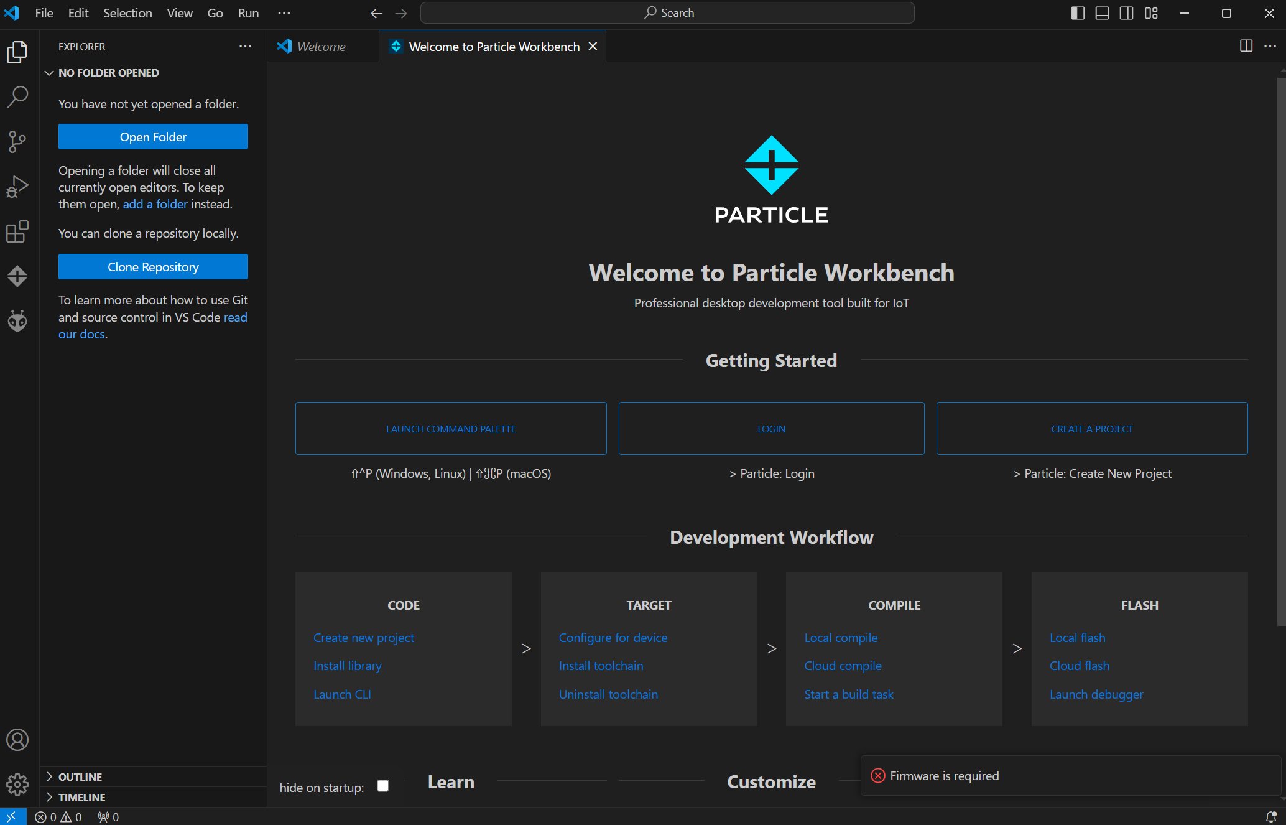
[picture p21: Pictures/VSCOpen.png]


Choose the entire project folder from the cloned repo (don't just open the .cpp or the src folder).

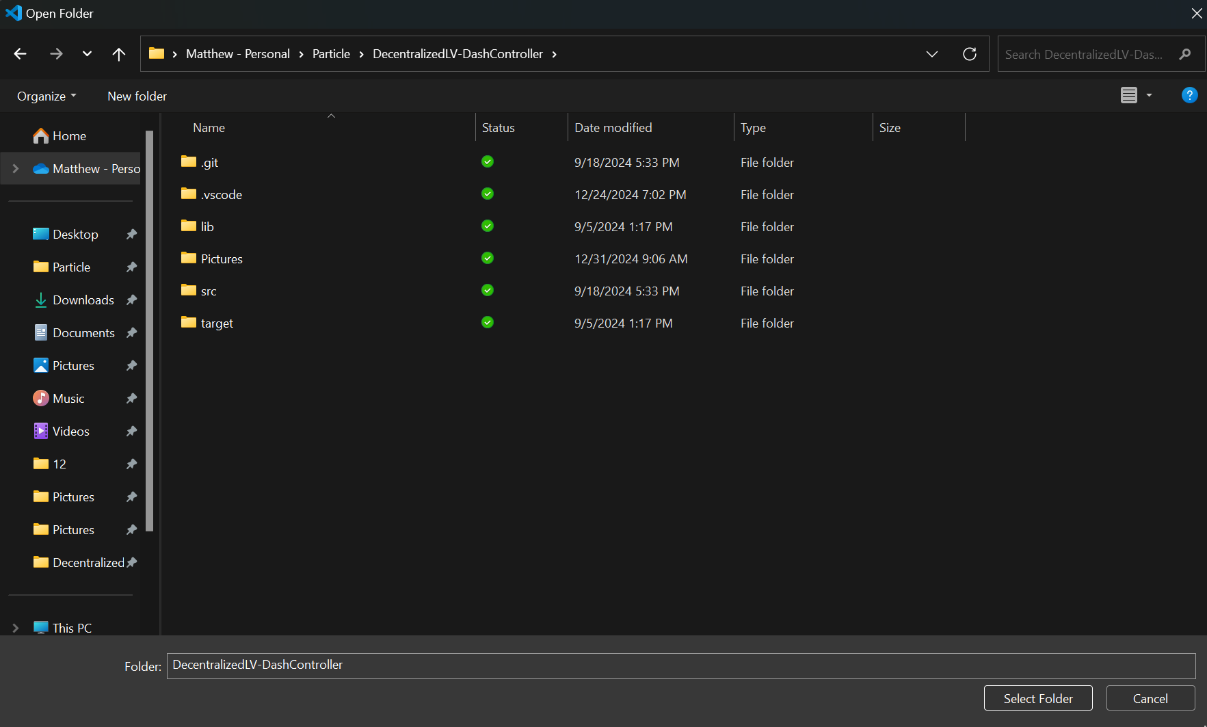
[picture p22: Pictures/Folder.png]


Once you've opened the folder, go to the Explorer tab on the left toolbar and expand the "src" folder. This folder will contain the source code for the program. Depending on how new your project is, there may be a .ino and a .cpp, or just a .cpp file. If there is a .ino file, open that by double clicking on it.

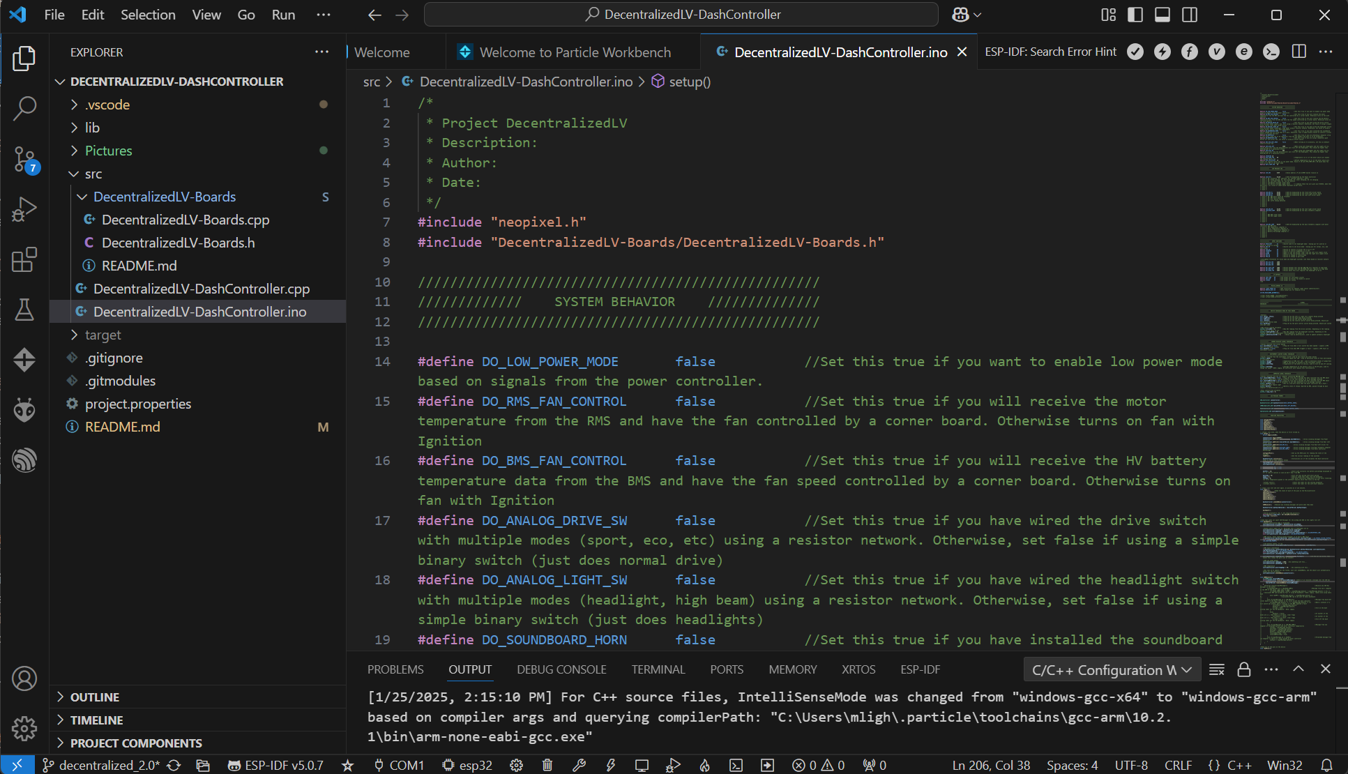
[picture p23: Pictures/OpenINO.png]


With the source file opened, some new options should appear in the top left corner of VS Code. These are used to compile and flash the application to the device. If these do not appear, you may have opened the incorrect folder.

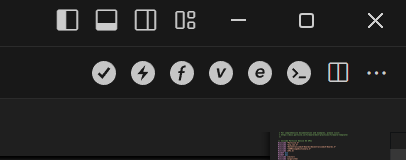
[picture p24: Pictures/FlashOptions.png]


Before we can flash the application though, please make sure the options are set up correctly for your microcontroller. To choose a platform, go to the bottom toolbar of VS Code, and there is a platform selection. Change this to whichever microcontroller you are using (BSoM, Photon, Photon 2, Xenon, Argon, P2, etc.).

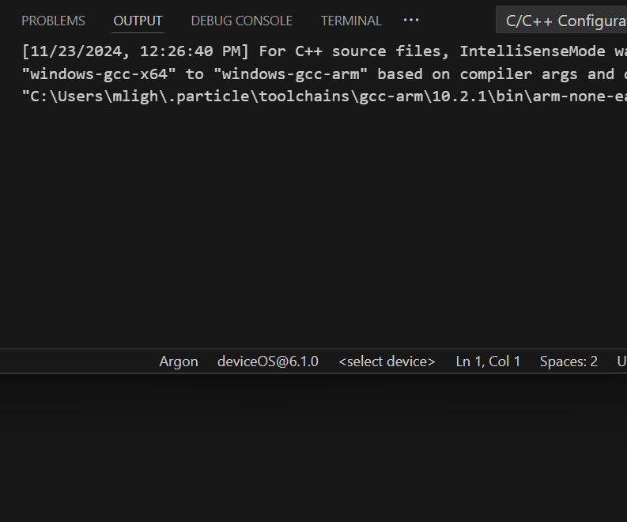
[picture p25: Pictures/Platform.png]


Next, connect your device using a USB cable to your computer. If you haven't registered the Particle device, its LED will be blinking blue. To set it up, follow Particle's [device setup process](https://setup.particle.io/). After registering with Particle, you will need to log in to Workbench by pressing Ctrl+Shift+P and doing Particle: Login. You'll need to log in for the flash tool to auto-detect your Particle device over USB, however there is a workaround. 

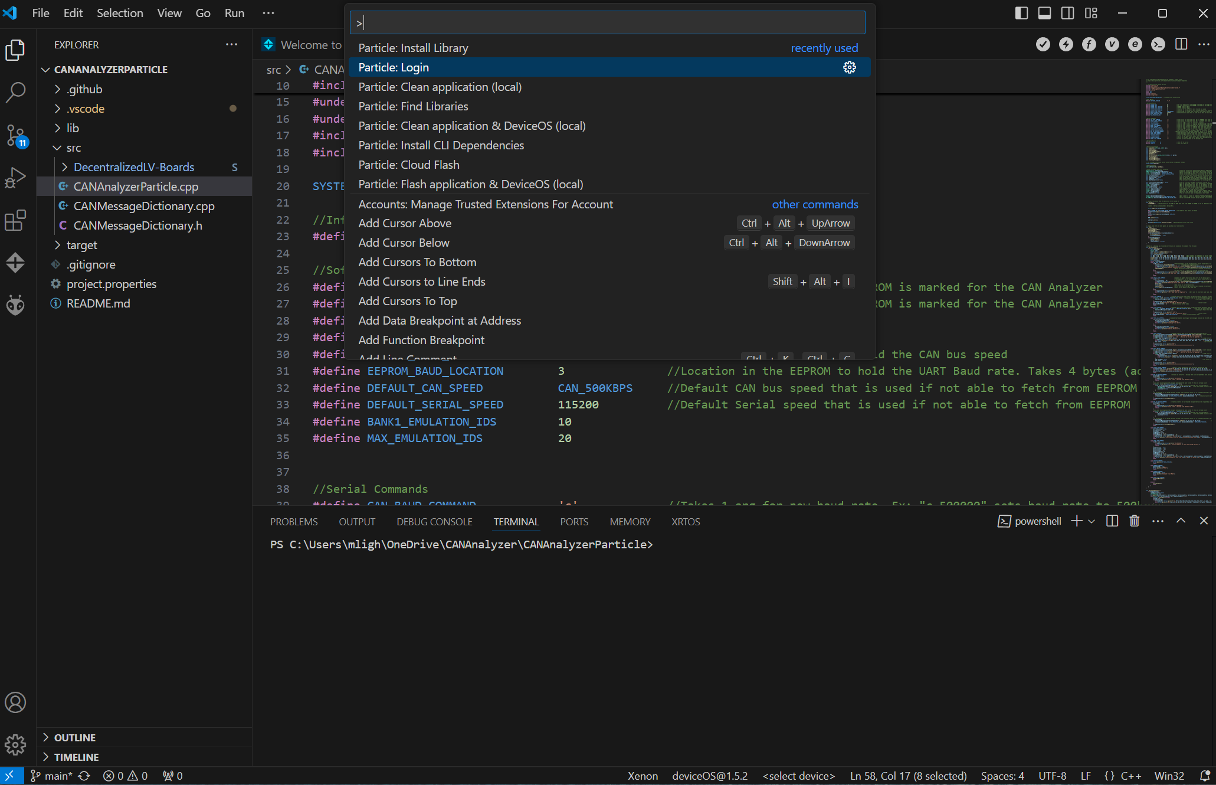
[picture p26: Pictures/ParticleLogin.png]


If your device has already had the Particle setup done on it, you can put it in DFU mode by pressing MODE and RESET, and then releasing RESET. Continue holding MODE until the LED is blinking yellow. From here you can flash the device. This is done by pressing the lightning bolt icon in the top right toolbar as previously shown. The output window will show the progress of the flash operation

**Important Note**: For the water vehicle code, ensure that you have [updated the bot number](#water-vehicle-identifier) before flashing! This is a unique ID used to identify the vehicle in the network

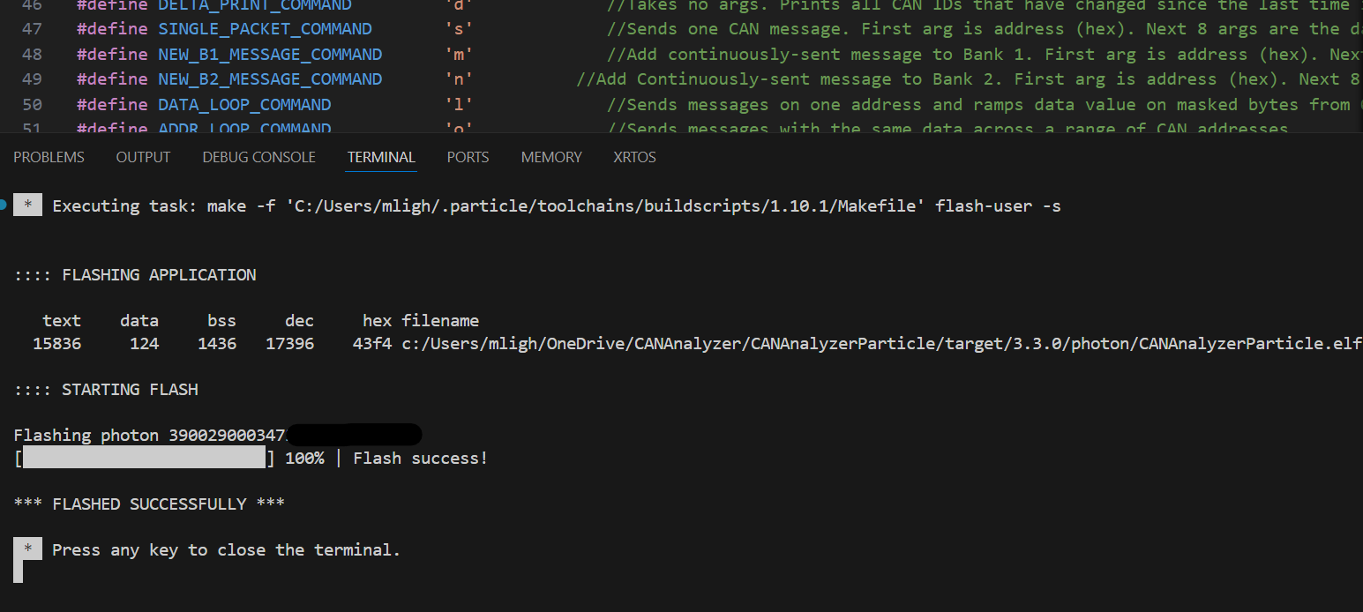
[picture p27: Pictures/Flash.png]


With the device flashed, you should now be running the new firmware.

### Installing Libraries

Most of the projects already have the MCP2515 and Neopixel libraries installed, but you may need to install others depending on your needs. To install a library, find the name of the library at [Particle's page](https://docs.particle.io/reference/device-os/libraries/search/). Then in VS Code, press Ctrl+Shift+P and find "Particle: Install Library". Enter the name and press enter. You must be logged into your Particle account (Ctrl+Shift+P Particle: Login) in VS Code to properly fetch the libraries! Libraries are installed under the `lib` folder.

## Software Architecture

### Microcontroller Datasheets

Check out the datasheets of each of the microcontrollers used on the boards in this system to better understand their capability and pinouts

- **[B402 Datasheet](https://docs.particle.io/reference/datasheets/b-series/b404-b402-datasheet/)**
- **[B404X Datasheet](https://docs.particle.io/reference/datasheets/b-series/b404x-datasheet/)**
- **[M.2 SoM Expansion Board](https://docs.particle.io/reference/datasheets/b-series/b-series-eval-board/)**

### Programming Reference Guide

This large programmer reference from Particle explains what each function in their software does and which pins those functions can be used on. 

**[Particle Device OS Reference](https://docs.particle.io/reference/device-os/firmware/)**

### Code Flow

Programs using Particle's DeviceOS follow the same setup used on Arduino, a `setup()` and `loop()` architecture. `setup()` is run once on startup, and then `loop()` continues executing forever as fast as it can. There can also be interrupts that pause this execution, jump to another function to execute some code, and then return to where it left off. These can be triggered by either a [Software Timer](https://docs.particle.io/reference/device-os/api/software-timers) or a [Pin Interrupt](https://docs.particle.io/reference/device-os/api/interrupts/interrupts).

**Caution**: The DecentralizedLV System can be controlling safety-critical operations. You need to ensure your code is responsive to messages coming in from the CAN Bus or is responding to switches from the driver.

To ensure that your code is responsive, you will need to be careful when adding any kind of delays in your program. It is not recommended to use `delay()`! This will cause what is known as blocking, where the controller sits idle and does not take inputs. Instead, you will want to use either [Software Timers](https://docs.particle.io/reference/device-os/api/software-timers), [Pin Interrupts](https://docs.particle.io/reference/device-os/api/interrupts/interrupts), or [millis()](https://docs.particle.io/reference/device-os/api/time/millis/) to schedule when operations should happen

Let's take an example of a program that we want to read a pin and change an LED to Green if the button is pressed. We also want the program to print a message once every second over the `Serial` console. Here's an example of why a `delay()` would cause problems:

```cpp
#define MYPIN_NUMBER    D0  //Microcontroller pin the voltage divider output is connected to
bool myPinSense;

void setup(){                         //Run once on startup
    pinMode(MYPIN_NUMBER, INPUT);     //Set GPIO to be an input
    RGB.control(true);                //Take control of the onboard RGB LED
    Serial.begin(9600);               //Start serial communication at 9600 baud
}

void loop(){                          //Continuously executes
    myPinSense = digitalRead(MYPIN_NUMBER);   //Read the state of the input signal
    if(myPinSense){             //If myPinSense is true, the button was pressed when digitalRead was called
        RGB.color(0, 255, 0);   //Takes R, G, B as arguments. This sets the LED to green
    }
    else{                       //If myPinSense is false, the button was released when digitalRead was called
        RGB.color(255, 255, 0); //Takes R, G, B as arguments. This sets the LED to green
    }
    delay(1000);    //Program sits for 1000 milliseconds
    //During this delay, NOTHING happens. The microcontroller is not reading the state of the pin.
    Serial.println("Print once per second!");   //Print out our message every one second
}
```

In this instance, if the button were only pressed for 250ms, the program may entirely miss it, as the button is only *sampled* every 1000ms due to the delay. This next example will utilize a `millis()` timing trick to trigger the print statement but have the button sampled much faster. `millis()` returns the number of milliseconds since the program started executing. This timing trick uses a variable to store a "snapshot" of the `millis()` clock and compare it against the current value of `millis()` to see how long it's been since the snapshot was taken.

```cpp
#define MYPIN_NUMBER    D0  //Microcontroller pin the voltage divider output is connected to
bool myPinSense;
uint32_t clockSnapshot = 0;

void setup(){                         //Run once on startup
    pinMode(MYPIN_NUMBER, INPUT);     //Set GPIO to be an input
    RGB.control(true);                //Take control of the onboard RGB LED
    Serial.begin(9600);               //Start serial communication at 9600 baud
}

void loop(){                          //Continuously executes
    myPinSense = digitalRead(MYPIN_NUMBER);   //Read the state of the input signal
    if(myPinSense){             //If myPinSense is true, the button was pressed when digitalRead was called
        RGB.color(0, 255, 0);   //Takes R, G, B as arguments. This sets the LED to green
    }
    else{                       //If myPinSense is false, the button was released when digitalRead was called
        RGB.color(255, 255, 0); //Takes R, G, B as arguments. This sets the LED to green
    }
    //NO delay!

    //Look at the difference between the snapshot and the actual clock
    // If the difference is > 1000, then 1000ms has elapsed.
    if(millis() - clockSnapshot > 1000){
        clockSnapshot = millis();                   //Take a NEW snapshot of the clock to reset the timer!
        Serial.println("Print once per second!");   //Print out our message every one second
    }
    //Now this loop() function executes thousands of times per second, making the button far more responsive!
}
```

This new mechanism is pretty simple to implement, and multiple snapshot variables can be created for timing different tasks. There is another implementation that can be done using a [Software Timer](https://docs.particle.io/reference/device-os/api/software-timers). The software timer will be set up to trigger every 1000ms and will set a boolean variable (called a "flag") to true, which will be read by the `loop()` function to check if 1000ms has elapsed.

```cpp
#define MYPIN_NUMBER    D0  //Microcontroller pin the voltage divider output is connected to
bool myPinSense;
bool timerDinged = false;

Timer myTimer(1000, timer_ding);      //Set up a timer and set its interval to 1000ms

void setup(){                         //Run once on startup
    pinMode(MYPIN_NUMBER, INPUT);     //Set GPIO to be an input
    RGB.control(true);                //Take control of the onboard RGB LED
    Serial.begin(9600);               //Start serial communication at 9600 baud
    myTimer.start();                  //Starts the timer. It will continuously execute until stop() is called
}

void loop(){                          //Continuously executes
    myPinSense = digitalRead(MYPIN_NUMBER);   //Read the state of the input signal
    if(myPinSense){             //If myPinSense is true, the button was pressed when digitalRead was called
        RGB.color(0, 255, 0);   //Takes R, G, B as arguments. This sets the LED to green
    }
    else{                       //If myPinSense is false, the button was released when digitalRead was called
        RGB.color(255, 255, 0); //Takes R, G, B as arguments. This sets the LED to green
    }
    //NO delay!

    if(timerDinged){            //Check if the timer function set the flag
        timerDinged = false;                        //Reset the flag until the timer sets it again
        Serial.println("Print once per second!");   //Print out our message every one second
    }
    //Now this loop() function executes thousands of times per second, making the button far more responsive!
}

void timer_ding(){
    timerDinged = true;
}
```

You can create multiple software timers in one program and have them set to different intervals for performing different tasks. In software timers, you can do other tricks, such as incrementing a variable, if you want to perform animations. One example would be to ramp up the value of a PWM output over time to fade an LED from off to on. Another good mechanism for reducing delay interference would be `attachInterrupt` which can be used to have a function trigger when a button is pressed. In this case, we will be changing the color of the LED in the function triggered by the button.

```cpp
#define MYPIN_NUMBER    D0  //Microcontroller pin the voltage divider output is connected to
bool myPinSense;
uint32_t clockSnapshot = 0;

void setup(){                                               //Run once on startup
    pinMode(MYPIN_NUMBER, INPUT);                           //Set GPIO to be an input
    RGB.control(true);                                      //Take control of the onboard RGB LED
    Serial.begin(9600);                                     //Start serial communication at 9600 baud
    attachInterrupt(MYPIN_NUMBER, pin_release, FALLING);    //call pin_release when the voltage falls
    attachInterrupt(MYPIN_NUMBER, pin_press, RISING);       //call pin_rising when the voltage rises
}

void loop(){                                                //Continuously executes
    //Look at the difference between the snapshot and the actual clock
    // If the difference is > 1000, then 1000ms has elapsed.
    if(millis() - clockSnapshot > 1000){
        clockSnapshot = millis();                           //Take a NEW snapshot of the clock to reset the timer!
        Serial.println("Print once per second!");           //Print out our message every one second
    }
    //Now this loop() function executes thousands of times per second, making the button far more responsive!
}

//function automatically called when pin is released
void pin_release(){
    RGB.color(255, 255, 0); //Takes R, G, B as arguments. This sets the LED to green
}

//function automatically called when pin is pressed
void pin_press(){
    RGB.color(0, 255, 0);   //Takes R, G, B as arguments. This sets the LED to green
}
```

### Some Noteworthy Functions from the Reference Guide

- [pinMode()](https://docs.particle.io/reference/device-os/api/input-output/pinmode) - configure pins as input or output
- [digitalWrite()](https://docs.particle.io/reference/device-os/api/input-output/digitalwrite) - set the output to 0V or 3.3V
- [digitalRead()](https://docs.particle.io/reference/device-os/api/input-output/digitalread) - Read if the input is 0V or 3.3V
- [analogRead()](https://docs.particle.io/reference/device-os/api/input-output/analogread-adc) - Read the voltage level of a pin between 0V and 3.3V as an integer between 0 and 4095
- [analogWrite()](https://docs.particle.io/reference/device-os/api/input-output/analogwrite-pwm) - Output a PWM signal. Takes one argument (0-255) to represent duty cycle
- [millis()](https://docs.particle.io/reference/device-os/api/time/) - Returns number of milliseconds since microcontroller started running. Use this for better timing compared to `delay()`!
- [attachInterrupt()](https://docs.particle.io/reference/device-os/api/interrupts/attachinterrupt) - Have a function automatically trigger when an input pin changes state
- [Timers](https://docs.particle.io/reference/device-os/api/software-timers) - Automatically trigger a function at a fixed interval
- [RGB](https://docs.particle.io/reference/device-os/api/led-signaling/) - Take control of the onboard RGB LED for easy onboard debugging
- [Serial](https://docs.particle.io/reference/device-os/api/serial) - Print out messages to a console for debugging with `Serial.printf()`
- [SPI](https://docs.particle.io/reference/device-os/api/spi) - Communicate with SPI peripherals like LCDs and the MCP2515
- [I2C](https://docs.particle.io/reference/device-os/api/wire-i2c) - Communicate with I2C sensors and peripherals
- [Cellular](https://docs.particle.io/reference/device-os/api/cellular) - Requires network setup. Allows for publishing data to the Particle Cloud or with Webhooks

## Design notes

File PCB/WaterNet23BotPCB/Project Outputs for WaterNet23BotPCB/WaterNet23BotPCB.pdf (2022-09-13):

Line # | Name | Description | Designator | Quantity | Value | Footprint | Manufacturer 1 | Manufacturer Part Number 1 | Manufacturer Lifecycle 1 | Supplier 1 | Supplier Part Number 1 | Supplier Unit Price 1 | Supplier Subtotal 1
| Capacitor | Capacitor | C1, C2, C3, C6, C7, C8, C16, C24 | | 8 1uF, 6.3V | ANTC1608X90N | Walsin Technologies | 0603X105K500CT | Unknown | Mouser | 791-0603X105K500CT | 0.053 | 1.27
| Capacitor | Capacitor | C4, C5, C9, C15, C17, C23, C25 | | 7 0.1uF, 6V | ANTC1608X90N | Samsung | CL10B104KB8NNWC | Volume Production | Mouser | 187-CL10B104KB8NNWC | 0.011 | 0.231
| Capacitor | Capacitor | C10, C18, C26 | | 3 47uF, 6.3V | ANTC1608X90N | Murata | GRM188R60J476ME15D | Volume Production | Newark | 92AH5102 | 0.127 | 1.14
| Capacitor | Capacitor | C11, C19, C27 | | 3 22uF, 6.3V | ANTC1608X90N | Samsung | CL10A226MP8NUNE | Volume Production | Mouser | 187-CL10A226MP8NUNE | 0.079 | 0.79
| Capacitor | Capacitor | C12, C20, C28 | | 3 4.7pF, 6.3V | ANTC1608X90N | Samsung | CL10C4R7BB8NNNC | Volume Production | Mouser | 187-CL10C4R7BB8NNNC | 0.035 | 0.35
| Capacitor | Capacitor | C13, C14, C21, C22, C29, C30, C34, C35, C36, C37, C38, C39, C40, C41 | | 14 10uF, 50V | CAPC2012X145N | Murata | GRM21BR61H106KE43L | Unknown | Newark | 64AJ4400 | 0.094 | 3.95
| Capacitor | Capacitor | C31, C32, C33 | | 3 4.7uF, 25V | ANTC1608X90N | Murata | GRM188R6YA475ME15D | Volume Production | Mouser | 81-GRM188R6YA475ME5D | 0.213 | 2.13
| BAV23CLT1G | Dual High Voltage Common Cathode Switching Diodes, 3-Pin SOT-23, Pb-Free, Tape and Reel | D1 | | 1 | ONSC-SOT-23-3-318-08_V | ON Semiconductor | BAV23CLT1G | Volume Production | Digi-Key | BAV23CLT1GOSCT-ND | 0.26 | 0.78
| >2A peak, >400mA cont. | Shottky Diode | D2, D3, D4 | | 3 | DIO_SS26FL | ON Semiconductor / Fairchild | SS26FL | Volume Production | Digi-Key | SS26FLCT-ND | 0.299 | 2.99
| USB4105-GF-A | USB-C (USB TYPE-C) USB 2.0 Receptacle Connector 24 (16+8 Dummy) Position Surface Mount, Right Angle; Through Hole | J1 | | 1 | GCT_USB4105-GF-A | Global Connector Technology | USB4105-GF-A | Unknown | Newark | 86AH2021 | 0.754 | 2.26
| uSD SPI Mode | 9 (8 + 1) Position Card Connector microSDâ„¢ Surface Mount, Right Angle Gold, 1.95mm profile, Normally open switch, Push push, Top mount | J2 | | 1 | GCT_MEM2051-00-195-00-A | Global Connector Technology | MEM2051-00-195-00-A | Unknown | Newark | 05W3557 | 0.748 | 2.24
| PCB.SMAFRA.HT | CONN SMA JACK R/A 50OHM PCB | J3, J4, J5, J6, J7 | | 5 | FP-PCB_SMAFRA_HT-MFG | Taoglas | PCB.SMAFRA.HT | Volume Production | Digi-Key | 931-1361-ND | 3.41 | 51.15
| Inductor | Inductor | L1, L2, L3 | | 3 4.7uH, >3A | IND_NR6028T4R7M | Taiyo Yuden | NR6028T4R7M | Volume Production | Newark | 09P6309 | 0.155 | | 1.4
| Inductor | Inductor | L4, L5, L6 | | 3 100uH, >2A | INDPM125125X800N | Bourns | SRR1280-101M | Volume Production | Mouser | 652-SRR1280-101M | 1.04 | 10.4
| XBP9B-DMUTB002 | RX TXRX MOD ISM < 1GHZ U.FL TH | MD1 | | 1 | FP-XBP9B-DMUTB002-MFG | Digi International | XBP9B-DMUTB002 | Volume Production
| Board Pwr, XT30 | Header, 2-Pin | P1 | | 1 | XT30_Horizontal | DFRobot | FIT0586 | Unknown | Digi-Key | 1738-1436-ND | | 1.9 | 5.7
| Pwr Button | Header, 2-Pin | P2 | | 1 | TE_6-440054-2 | TE Connectivity | 440054-2 | Volume Production | Newark | 88W2432 | 0.035 | 0.105
| Solar Panel Converter | Header, 2-Pin | P3 | | 1 | XT30_Horizontal | DFRobot | FIT0586 | Unknown | Digi-Key | 1738-1436-ND | | 1.9 | 5.7
| Motor 1 | Header, 6-Pin | P4 | | 1 | TE_1586039-6 | TE Connectivity | 1586039-6 | Volume Production | Avnet | 1586039-6 | 0.30877 | 0.92631
| Motor 2 | Header, 6-Pin | P5 | | 1 | TE_1586039-6 | TE Connectivity | 1586039-6 | Volume Production | Avnet | 1586039-6 | 0.30877 | 0.92631
| LED Header | Header, 4-Pin | P6 | | 1 | TE_350761-4 | TE Connectivity | 350761-4 | Volume Production | Avnet | 350761-4 | 0.39093 | 1.17
| Sensor Probe Side | Header, 3-Pin | P7, P10, P11, P13, P15 | | 5 | 1x3 Header | Preci-Dip | 801-87-003-10-001101 | Volume Production | Farnell | 2839823 | 0.373 | | 5.6
| Sensor MCU Side | Header, 3-Pin | P8, P9, P12, P14, P16 | | 5 | 1x3 Header | Preci-Dip | 801-87-003-10-001101 | Volume Production | Newark | 49AC1404 | 0.376 | 5.64
| 2x Debug | Header, 2-Pin | P17, P18, P20, P21, P22, P23 | | 6 | 1x2 Header
| Header 4X2 | Header, 4-Pin, Dual row | P19 | | 1 | 4x2 Header
| Header 3X2 | Header, 3-Pin, Dual row | P24 | | 1 | 2x3 Header
| FDD6670A | N-Channel MOSFET | Q1 | | 1 | DPAK | ON Semiconductor / Fairchild | FDD6670A | Volume Production | Arrow Electronics | FDD6670A | 1.21 | 3.64
| YJL3400A | N-Channel MOSFET | Q2, Q3 | | 2 | SOT23-3 | Yangjie Electronic Technology | YJL3400A-F2-0000HF | Unknown | Digi-Key | 3191-YJL3400A-F2-0000HFCT-ND | 0.29 | 1.74
| Resistor | Resistor | R1, R2 | | 2 1k | ANTC1608X90N | Walsin Technologies | WR06X1001FTL | Volume Production | Newark | 58Y7257 | 0.005 | 0.03
| Resistor | Resistor | R3, R4 | | 2 5.1k | ANTC1608X90N | Stackpole Electronics | RMCF0603FT5K10 | Volume Production | Digi-Key | RMCF0603FT5K10CT-ND | 0.015 | 0.15
| Resistor | Resistor | R5, R10, R19 | | 3 50k | ANTC1608X90N | Yageo | RC0603FR-0749K9L | Volume Production | Newark | 82AH8171 | 0.011 | 0.11
| Resistor | Resistor | R6, R15, R21 | | 3 301k | ANTC1608X90N | Stackpole Electronics | RMCF0603FT301K | Volume Production | Digi-Key | RMCF0603FT301KCT-ND | 0.015 | 0.15
| Resistor | Resistor | R7, R16 | | 2 96.3k | ANTC1608X90N | Stackpole Electronics | RMCF0603FT95K3 | Volume Production | Arrow Electronics | RMCF0603FT95K3 | 0.0137 | 0.137
| Resistor | Resistor | R8 | | 1 1m | RESC6331X70N | Cyntec | SCMM2512S5-R001F | Unknown | Digi-Key | 2037-SCMM2512S5-R001FCT-ND | 0.92 | 2.76
| Resistor | Resistor | R9, R12, R14 | | 3 100k | ANTC1608X90N | Walsin Technologies | WR06X1003FTL | Volume Production | Newark | 68Y8438 | 0.001 | 0.01
| Resistor | Resistor | R11, R17, R20 | | 3 20k | ANTC1608X90N | Stackpole Electronics | RMCF0603JT20K0 | Volume Production | Digi-Key | RMCF0603JT20K0CT-ND | 0.014 | 0.14
| Resistor | Resistor | R13, R26, R27, R28, R29, R32, R33, R34, R35, R36, R37 | | 11 10k | ANTC1608X90N | Stackpole Electronics | RNCP0603FTD10K0 | Volume Production | Arrow Electronics | RNCP0603FTD10K0 | 0.0514 | | 1.7
| Resistor | Resistor | R18 | | 1 10m | RESC6331X70N | Rohm | PMR100HZPJU10L | Volume Production | Digi-Key | RHM.010AVCT-ND | 0.55 | 1.65
| Resistor | Resistor | R22 | | 1 80.3k | ANTC1608X90N | Yageo | RC0603FR-0780K6L | Volume Production | Mouser | 603-RC0603FR-0780K6L | 0.017 | 0.17
| Resistor | Resistor | R23, R24, R25 | | 3 30m, >0.1W | ANTC1608X90N | Panasonic | ERJ-3BWFR030V | Volume Production | Digi-Key | P17466CT-ND | 0.32 | | 3.2
| Resistor | Resistor | R30, R31 | | 2 200k | ANTC1608X90N | Stackpole Electronics | RMCF0603FT200K | Volume Production | Digi-Key | RMCF0603FT200KCT-ND | 0.015 | 0.15
| Switch Normally Opened | Switch Normally Opened | S1, S2 | | 2 | TL3313AF250QG | E-Switch | TL3313AF250QG | Volume Production | Mouser | 612-TL3313AF250QG | 0.45 | | 2.7
| B402 | Connector, Backplane, Housing, Receptacle, 67 Position, 2row | U1 | | 1 | B402 Full | TE Connectivity | 2199230-4 | Volume Production | Newark | 89W2151 | | 1.2 | 3.6
| ISL85003AFRZ | No Description Available | U2, U4, U6 | | 3 | SON50P300X300X100-13N(270X200) | Intersil | ISL85003AFRZ | Not Recommended for New Design
| INA139 | Current Monitor Regulator High-Side SOT-23-5 | U3, U5 | | 2 | INA139-Q1 | Texas Instruments | INA139QPWRQ1 | Volume Production

Line # | Name | Description | Designator | Quantity | Value | Footprint | Manufacturer 1 | Manufacturer Part Number 1 | Manufacturer Lifecycle 1 | Supplier 1 | Supplier Part Number 1 | Supplier Unit Price 1 | Supplier Subtotal 1
| AL8861Y-13 | LED Driver IC 1 Output DC DC Regulator Step-Down _Buck_ Analog, PWM Dimming 1.5A SOT-89-5 | U7, U8, U9 | | 3 | CONV_AL8861Y-13 | Diodes | AL8861Y-13 | Unknown | Arrow Electronics | AL8861Y-13 | 0.5059 | 5.06
| MAX14933ASE+T | | U10, U12, U14, U16 | | 4 | SOIC127P600X175-16N | Maxim | MAX14933ASE+T | Not Recommended for New Design | Mouser | 700-MAX14933ASE+T | | 5.3 63.6
| B0303S-1WR3 | 3V3 Isolator | U11, U13, U15, U17 | | 4 | B0303S-1WR3 | MORNSUN | B0303S-1WR3 | Unknown | Digi-Key | 2725-B0303S-1WR3-ND | 1.77 | 21.22

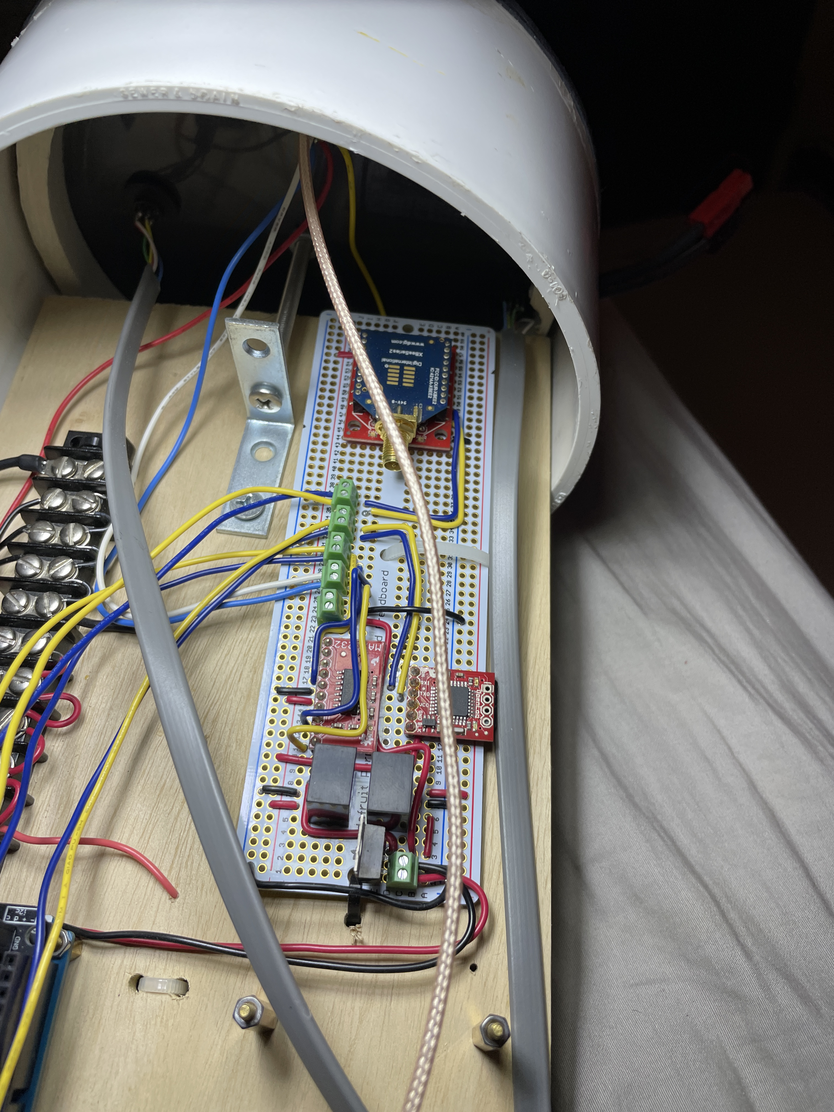
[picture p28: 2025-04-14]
Pictures/OriginalHardware.jpg

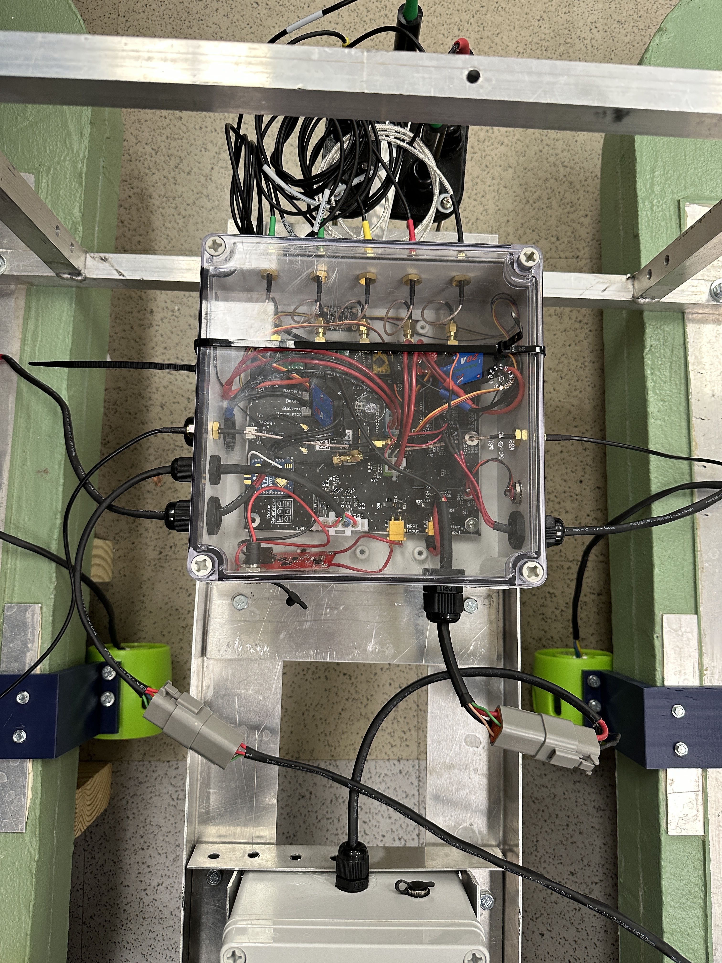
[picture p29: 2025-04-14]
Pictures/VehicleFrame.jpg

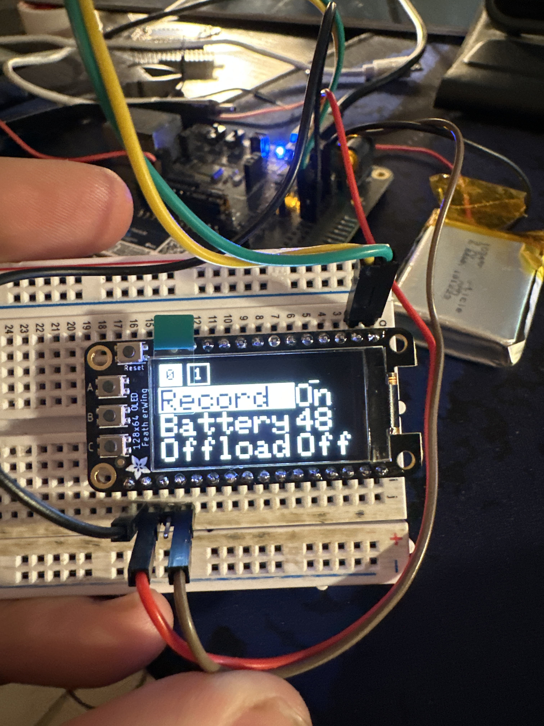
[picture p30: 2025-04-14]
Pictures/CCHub_Menu.jpg

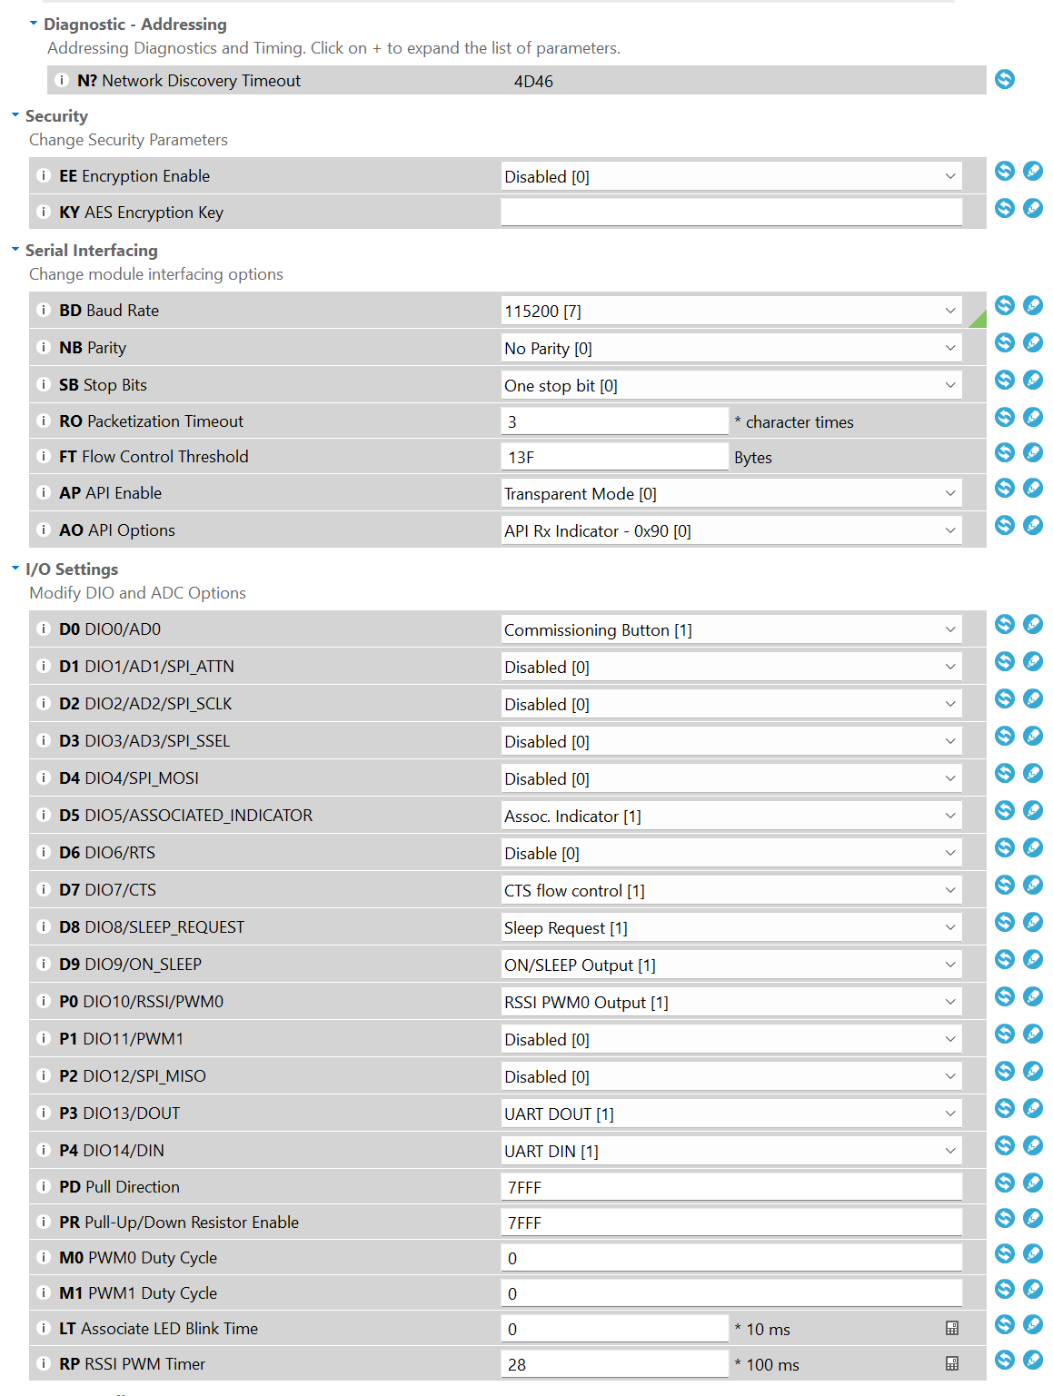
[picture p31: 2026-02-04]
Pictures/XCTU_ModuleSettings2.png

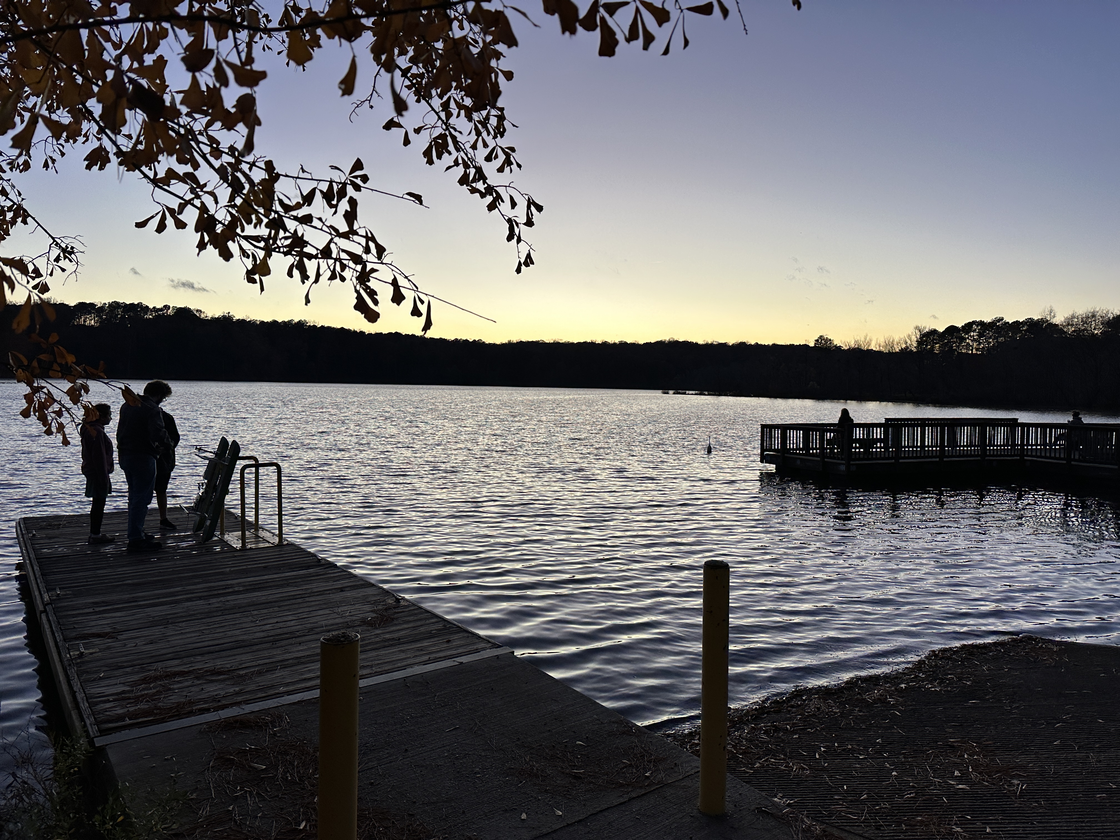
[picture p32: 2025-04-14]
Pictures/Lake.jpg

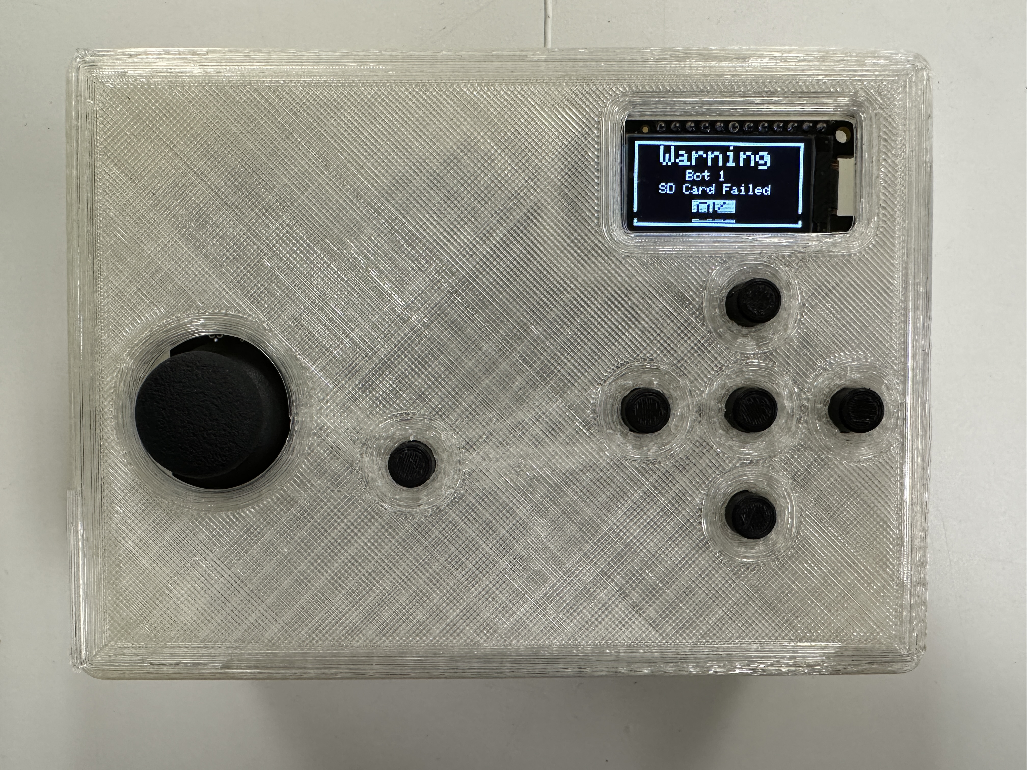
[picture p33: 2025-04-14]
Pictures/CCHub_Warning.jpg

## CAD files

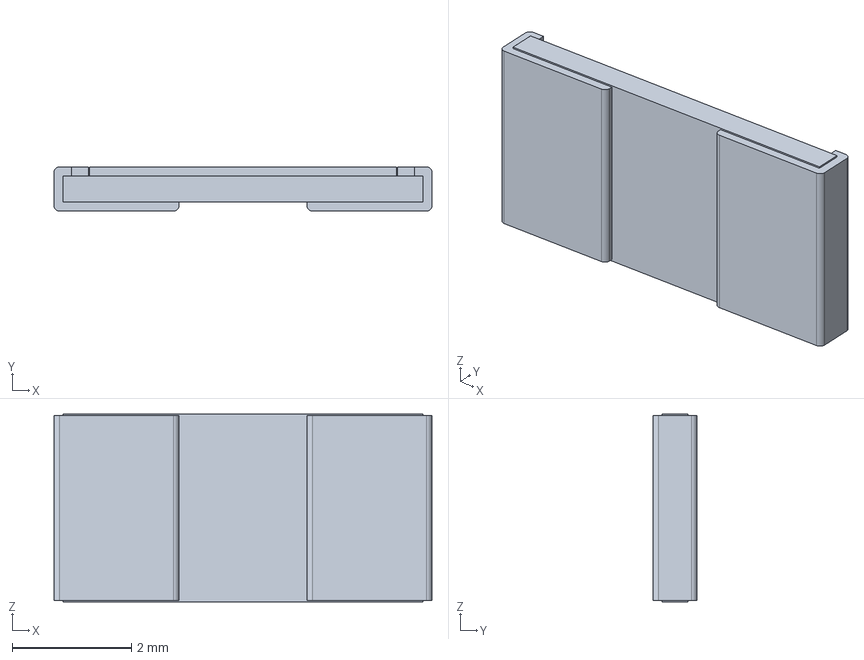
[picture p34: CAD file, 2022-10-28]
PCB/WaterNet23BotPCB/2512 Resistor/2512 Resistor.stp
6.35 x 0.74 x 3.15 mm

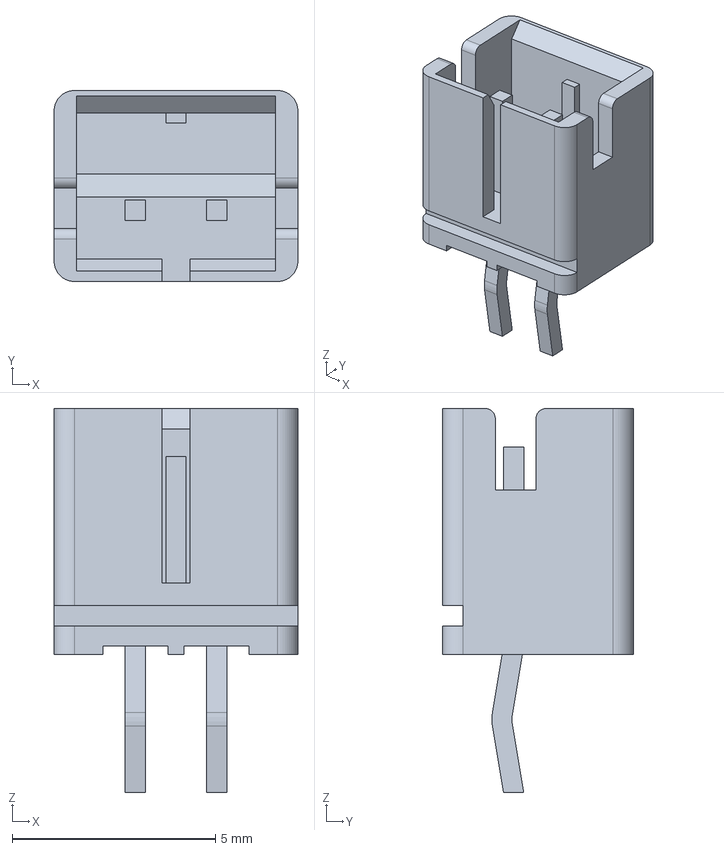
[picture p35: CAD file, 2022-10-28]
PCB/WaterNet23BotPCB/6-440054-2/6-440054-2.stp
6.00 x 4.70 x 9.45 mm

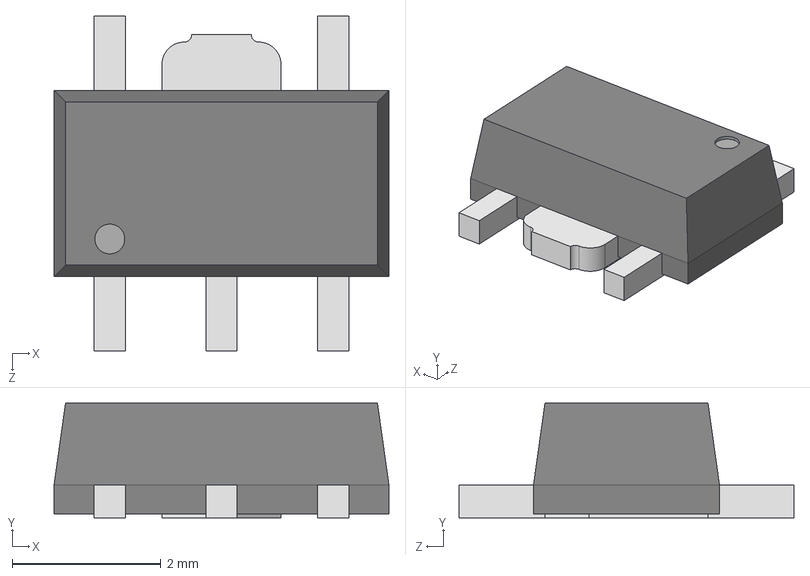
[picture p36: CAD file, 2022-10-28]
PCB/WaterNet23BotPCB/AL8861Y-13/SOT89-5.step
4.50 x 1.54 x 4.50 mm

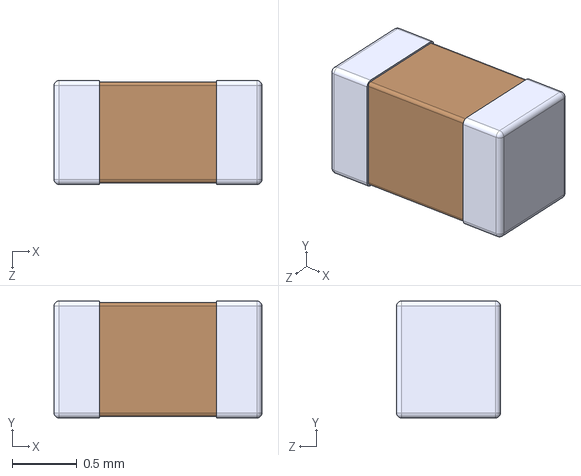
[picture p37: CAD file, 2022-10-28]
PCB/WaterNet23BotPCB/ANTC1608X90N/GGM188R71C105KA64D.STEP
1.60 x 0.9 x 0.8 mm

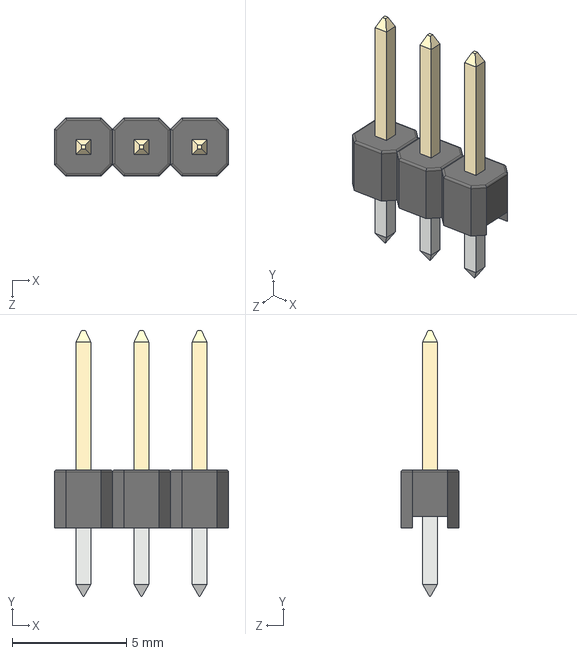
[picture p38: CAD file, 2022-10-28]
PCB/WaterNet23BotPCB/Extra Models/1-3_Header.STEP
7.62 x 11.6 x 2.54 mm
PR20203VBNN x 3

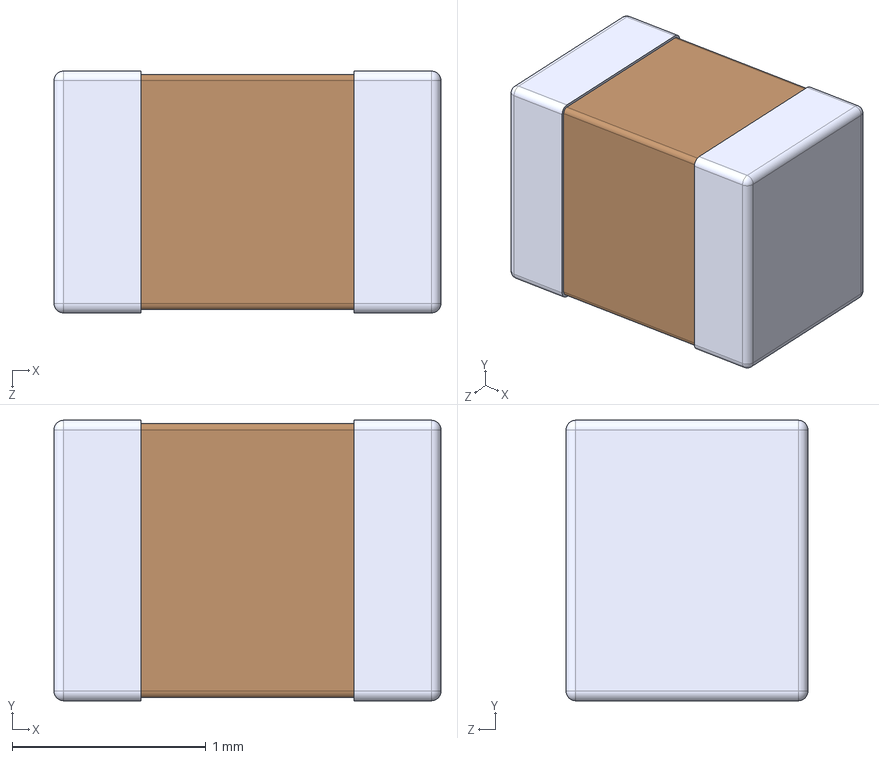
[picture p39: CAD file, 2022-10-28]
PCB/WaterNet23BotPCB/GRM21BR61H106KE43K/GRM21BR61H106KE43L.STEP
2.00 x 1.45 x 1.25 mm

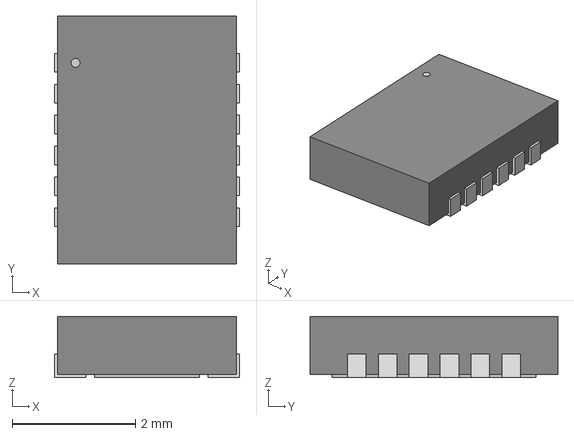
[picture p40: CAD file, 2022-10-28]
PCB/WaterNet23BotPCB/ISL85003AFRZ/DFN12_4X3_INR.step
3.00 x 4.01 x 0.993 mm

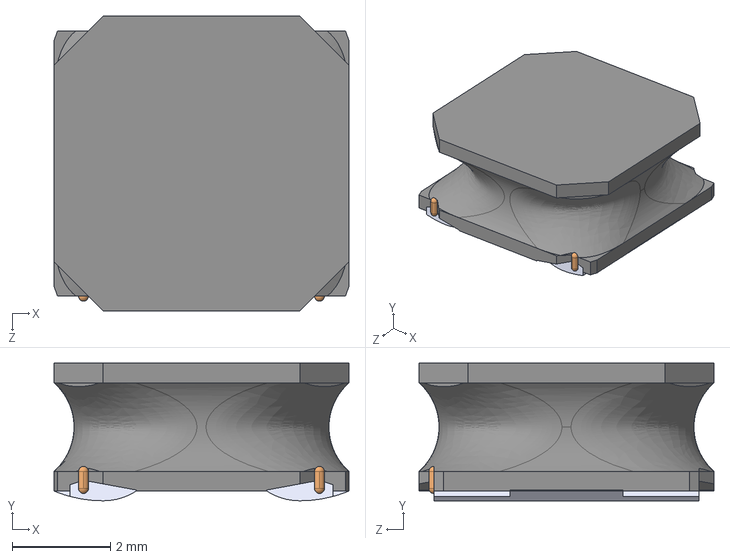
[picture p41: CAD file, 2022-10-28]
PCB/WaterNet23BotPCB/NR6028T4R7M/NR6028T4R7M--3DModel-STEP-56544.STEP
6.00 x 2.80 x 6.00 mm

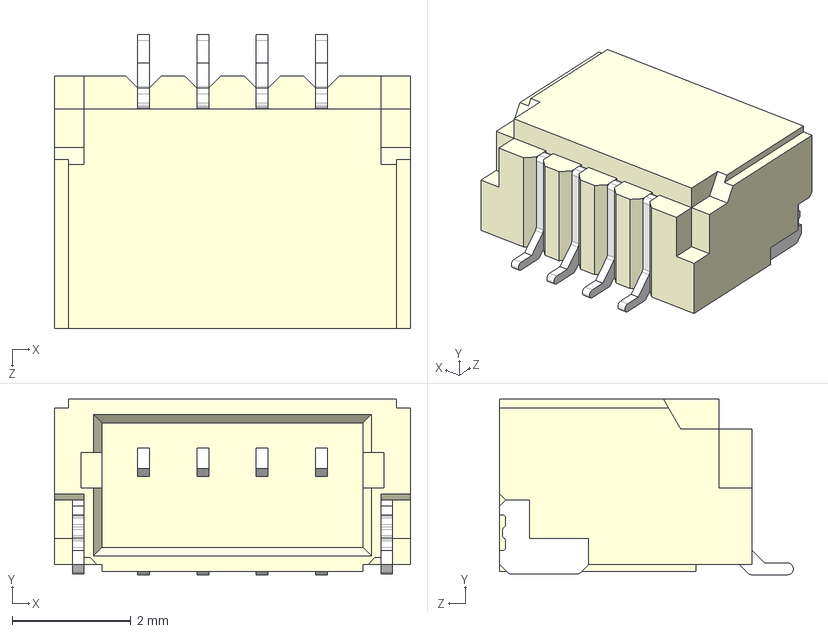
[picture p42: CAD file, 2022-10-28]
PCB/WaterNet23BotPCB/Quiic JST-SH-4/SM04B-SRSS-TB(LF)(SN)--3DModel-STEP-56544.STEP
6.00 x 2.96 x 4.95 mm

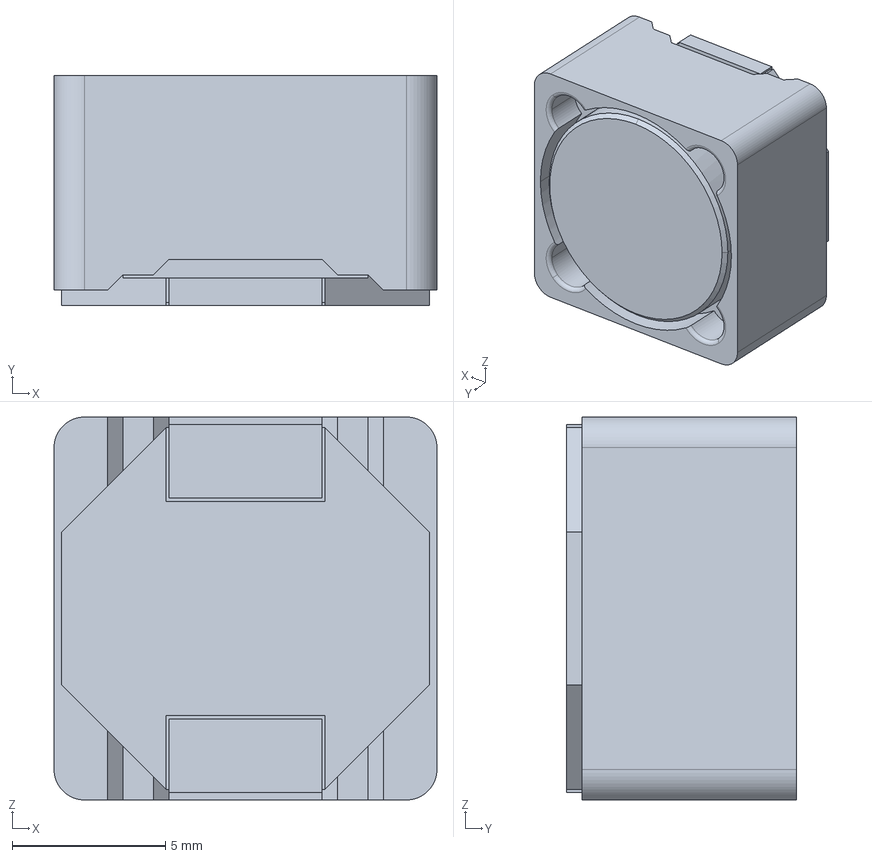
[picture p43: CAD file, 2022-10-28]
PCB/WaterNet23BotPCB/SRR1280-101M/srr1280-101m.stp
12.5 x 7.50 x 12.5 mm

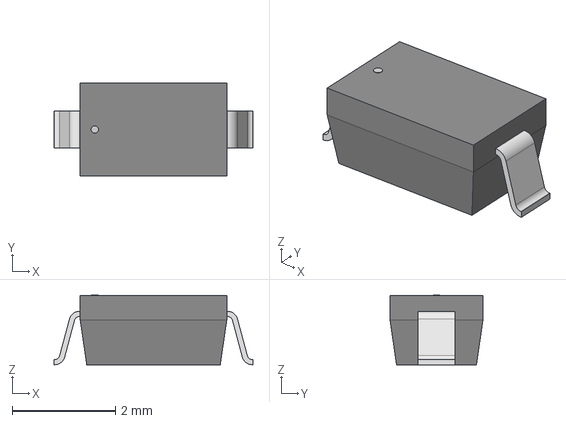
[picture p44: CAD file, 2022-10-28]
PCB/WaterNet23BotPCB/SS26FL/SOD-123_ONS.step
3.86 x 1.80 x 1.35 mm

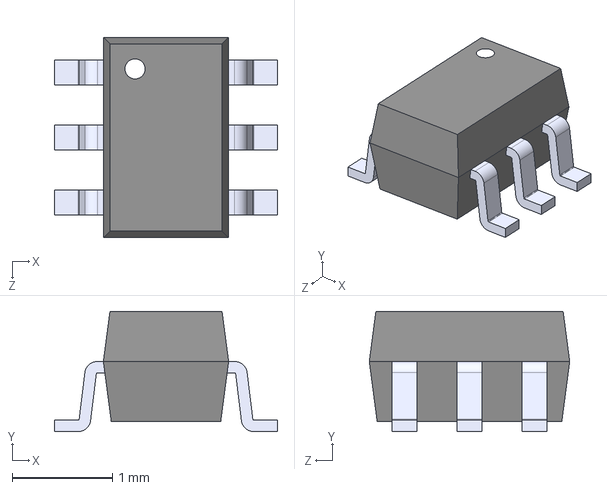
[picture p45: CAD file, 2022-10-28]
PCB/WaterNet23BotPCB/TSM2N7002KDCU6_RFG/TSM2N7002KDCU6 RFG--3DModel-STEP-554148.STEP
2.23 x 1.20 x 2.00 mm

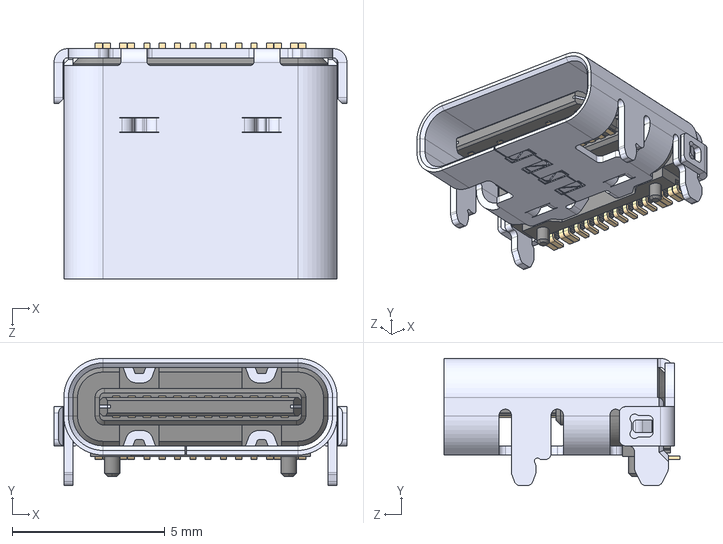
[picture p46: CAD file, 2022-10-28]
PCB/WaterNet23BotPCB/USB4105-GF-A/USB4105-GF-A--3DModel-STEP-56544.STEP
9.58 x 4.16 x 7.71 mm

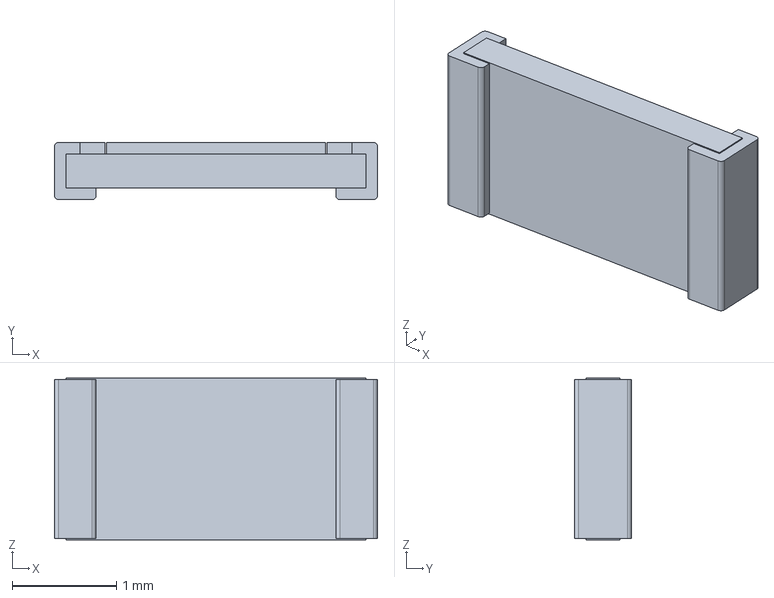
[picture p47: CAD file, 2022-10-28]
PCB/WaterNet23CCHUBPCB/1206 Package/Resistor 1206.stp
3.10 x 0.55 x 1.55 mm

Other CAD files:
PCB/WaterNet23BotPCB/K7803-3AR3/K78xx-3AR3.stp
PCB/WaterNet23BotPCB/1586039-6/1586039-6.stp
PCB/WaterNet23BotPCB/350761-4/350761-4.stp
PCB/WaterNet23BotPCB/Extra Models/1-3_Socket.STEP
PCB/WaterNet23BotPCB/Extra Models/2-3_Header.STEP
PCB/WaterNet23BotPCB/Extra Models/2-4_Header.stp
PCB/WaterNet23BotPCB/Extra Models/7-Pin Socket.stp
PCB/WaterNet23BotPCB/Extra Models/8-Pin Socket.stp
PCB/WaterNet23BotPCB/Extra Models/8-SOIC.step
PCB/WaterNet23BotPCB/Extra Models/Amass_XT30PW-M_pcb solder.stp
PCB/WaterNet23BotPCB/Extra Models/B402.step
PCB/WaterNet23BotPCB/Extra Models/DCDC Converter.STEP
PCB/WaterNet23BotPCB/Extra Models/IND_BOURNS_SRR1280.step
PCB/WaterNet23BotPCB/Extra Models/TL3313AF250QG--3DModel-STEP-520916.STEP
PCB/WaterNet23BotPCB/MAX14933ASE_T/MAX14933ASE+T.STEP
PCB/WaterNet23CCHUBPCB/Button/CUI_DEVICES_TS02-66-170-BK-260-SCR-D.step
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

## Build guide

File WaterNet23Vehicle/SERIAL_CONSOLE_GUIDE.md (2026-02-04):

# WaterNet23 Serial Console Interface

## Overview
The WaterNet23 vehicle now supports command input directly from the Serial console (COM port) in addition to XBee, BLE, and LTE communications. This provides a convenient way to interact with the vehicle during development, testing, and debugging.

## Getting Started

### Connecting to the Console
1. Connect the WaterNet23 vehicle to your computer via USB
2. Open a serial terminal (Arduino IDE Serial Monitor, PuTTY, etc.)
3. Configure: **115200 baud, 8N1**
4. After boot, you'll see the startup message:

```
=== WaterNet23 Bot 1 Console Ready ===
Type 'help' or 'hlp' for command list
Commands can be entered as: <cmd> <data>
Example: sim1, cms, ekf1, hlp
=====================================
```

### Command Formats
The console supports two command formats:

#### 1. Simple Format (Recommended)
Just type the command and data directly:
```
sim1
cms
ekf1
hlp
mtr090090
```

#### 2. Raw Format (Advanced)
Use the full protocol format:
```
B1CCsim1F
B1CCcms0E
B1CCekf1F
```

## Available Commands

### Basic System Commands
- **`help`** or **`hlp`** - Show command reference
- **`?`** - Alternative help command
- **`stp`** - Emergency stop (stops all motors immediately)

### Navigation & Control
- **`ctl <lat> <lon> <mode> <log> <led>`** - Set target position and drive mode
  - Example: `ctl 42.3601 -83.0732 1 1 0`
- **`mtr <lspeed><rspeed>`** - Control motors (3 digits each, 090 = stop)
  - Example: `mtr090090` (stop both), `mtr100080` (slow forward)

### Sensor & GPS
- **`req`** - Request current sensor data
- **`egp <lat> <lon>`** - Set emulated GPS position for testing
  - Example: `egp 42.3601 -83.0732`

### Compass System
- **`cms`** - Show compass manager status
- **`cms0`** - Switch to LSM303 compass
- **`cms1`** - Switch to LIS3MDL compass
- **`cms2`** - Auto-detect compass type
- **`cmp`** - Perform compass calibration

### Simulation System
- **`sim`** - Show simulation status
- **`sim0`** - Disable simulation (use real sensors)
- **`sim1`** - Enable static position simulation
- **`sim2`** - Enable waypoint navigation simulation
- **`sim3`** - Enable circular motion simulation
- **`sim4`** - Enable random walk simulation

### Extended Kalman Filter (EKF)
- **`ekf`** - Show EKF status
- **`ekf0`** - Disable EKF filtering
- **`ekf1`** - Enable EKF filtering
- **`ekf1 0.01 0.1`** - Enable EKF with custom noise parameters

### Debug & Utility
- **`pts <message>`** - Print message to console and log
  - Example: `pts Hello World`
- **`spc`** - Send status/ping
- **`dmp`** - Enter data dump mode for SD card offloading

## Interactive Examples

### Testing Simulation System
```
> sim
Simulation Status:
  Enabled: No
  Mode: 0

> sim1
> Simulation enabled: Static mode

> sim
Simulation Status:
  Enabled: Yes
  Mode: 1
  Current GPS: Lat=42.360100, Lon=-83.073200, Course=45.0
  Current Compass: Heading=45.0
```

### Compass Management
```
> cms
Compass Manager Status:
  Manager initialized: Yes
  Active compass: LIS3MDL
  Manager connected: Yes
  Current heading: 87.45

> cms0
> Switched to compass type: LSM303
```

### Motor Control
```
> mtr090090
> Emergency stop activated

> mtr100080
> Received Motor Command: LSpeed=100,RSpeed=80
```

### Getting Help
```
> help
=== WaterNet23 Vehicle Commands ===
[Full command reference displayed]

> ?
[Same help output]
```

## Features

### Command Echo
All commands are echoed back with a `>` prompt:
```
> sim1
> Simulation enabled: Static mode
```

### Error Handling
Invalid commands show helpful error messages:
```
> invalidcmd
Warning: Unknown command 'invalidcmd'
```

### Automatic Formatting
Simple commands are automatically formatted with proper bot addressing and checksums:
- Input: `sim1`
- Formatted: `B1CCsim1F` (for bot 1)

### Logging
All console commands are logged to the SD card for debugging and audit purposes.

## Integration with Existing Systems

### Works Alongside Other Communication Methods
- XBee (Serial1) - for wireless mesh communication
- BLE - for mobile app connectivity
- LTE - for cloud connectivity
- Serial Console - for direct development access

### Same Command Processing
Console commands use the same `processCommand()` function as other interfaces, ensuring consistent behavior across all communication methods.

### Mode Handling
Console commands are processed with mode `1` (similar to BLE), which means they have the same priority and handling as Bluetooth commands.

## Debugging Tips

### Enable Verbose Mode
Uncomment `#define VERBOSE` in the code to see detailed command processing:
```cpp
#define VERBOSE  // Add this line
```

### Monitor Command Flow
With verbose mode enabled, you'll see:
```
New Serial Console Command:
sim1
Formatted command: B1CCsim1F
Command: sim, Data: 1, Checksum: 0F
Simulation enabled: Static mode
```

### Check Logs
All console interactions are logged to the SD card file for later analysis.

## Troubleshooting

### No Response to Commands
1. Check baud rate (must be 115200)
2. Ensure line ending is set to newline (`\n`)
3. Verify bot number matches in commands

### Commands Not Recognized
1. Use `help` to see available commands
2. Check command spelling
3. Try raw format if simple format fails

### Simulation Not Working
1. Check simulation status with `sim`
2. Verify mode with status command
3. Use verbose output to debug

This Serial console interface significantly improves the development and testing experience by providing direct, real-time access to all vehicle systems without requiring wireless communication setup.

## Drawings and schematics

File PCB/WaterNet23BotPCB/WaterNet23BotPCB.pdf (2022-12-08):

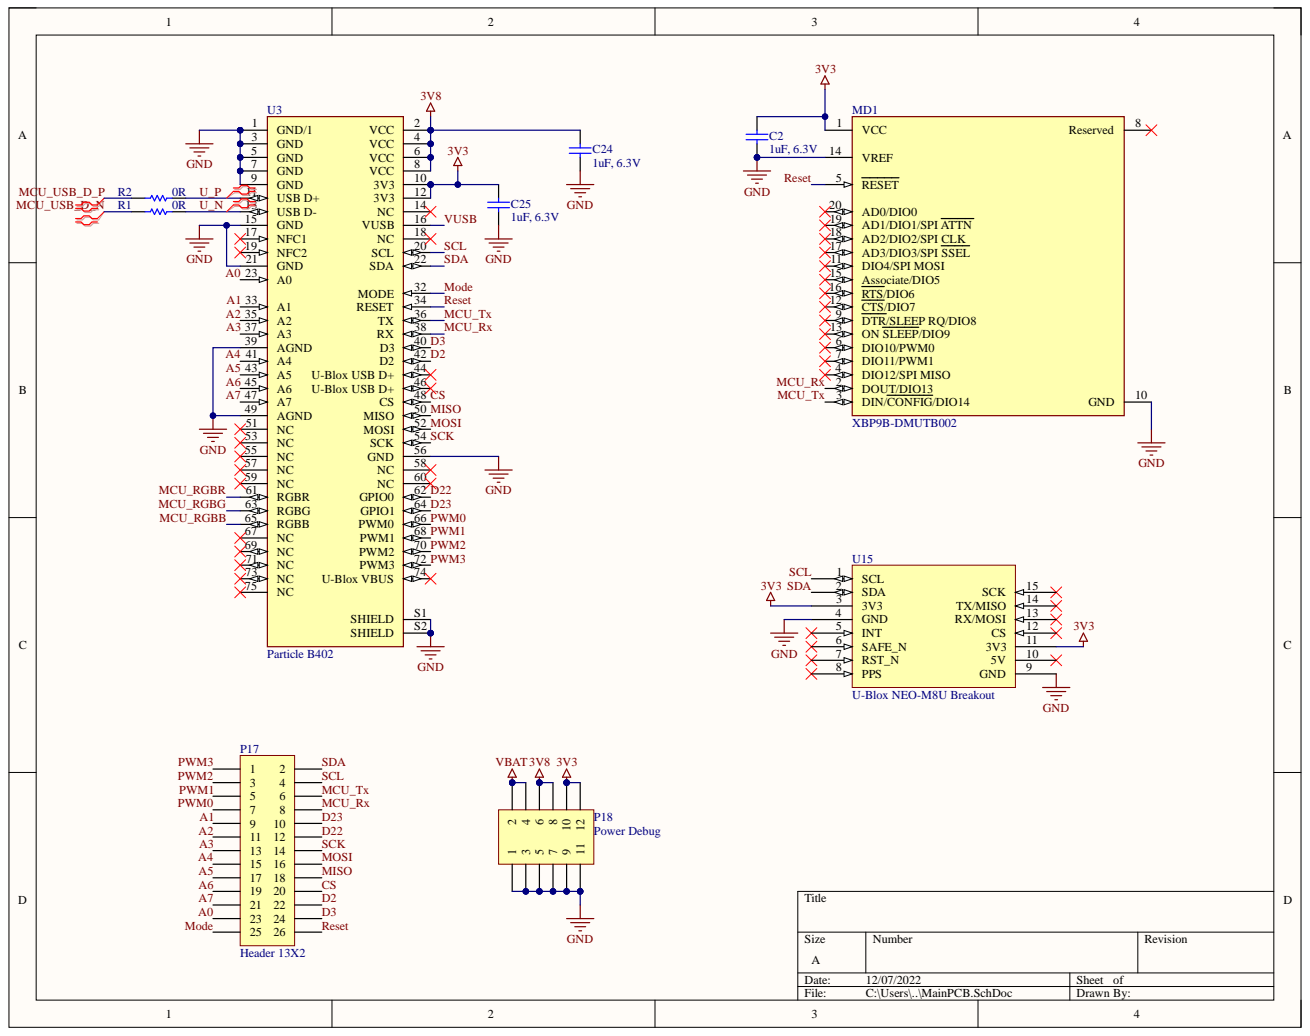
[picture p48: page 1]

3 | 4 | 3V 3

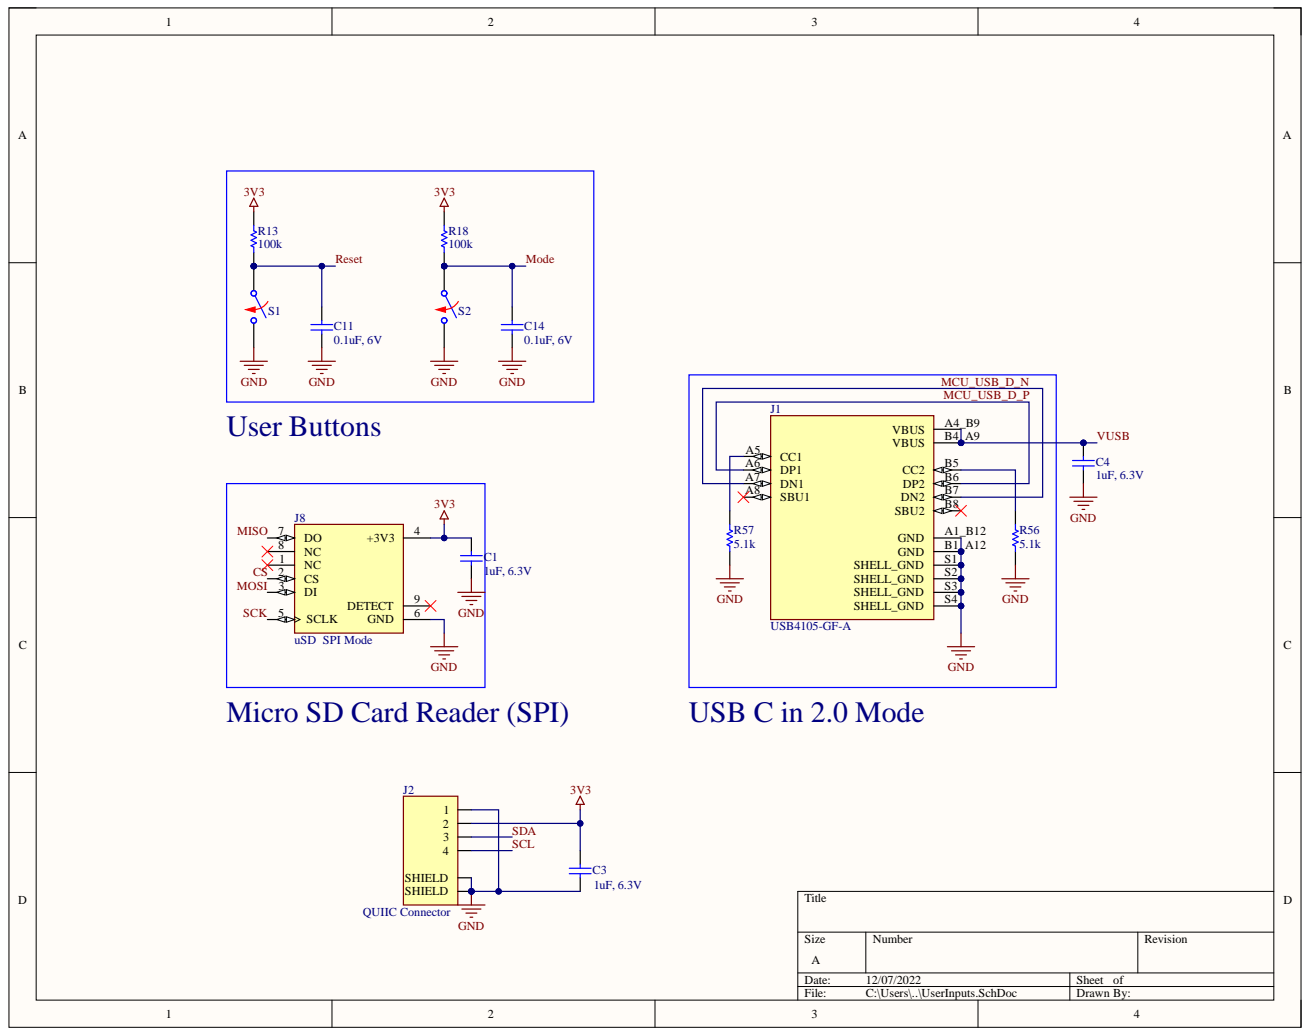
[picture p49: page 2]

Micro SD Card Reader (SPI)

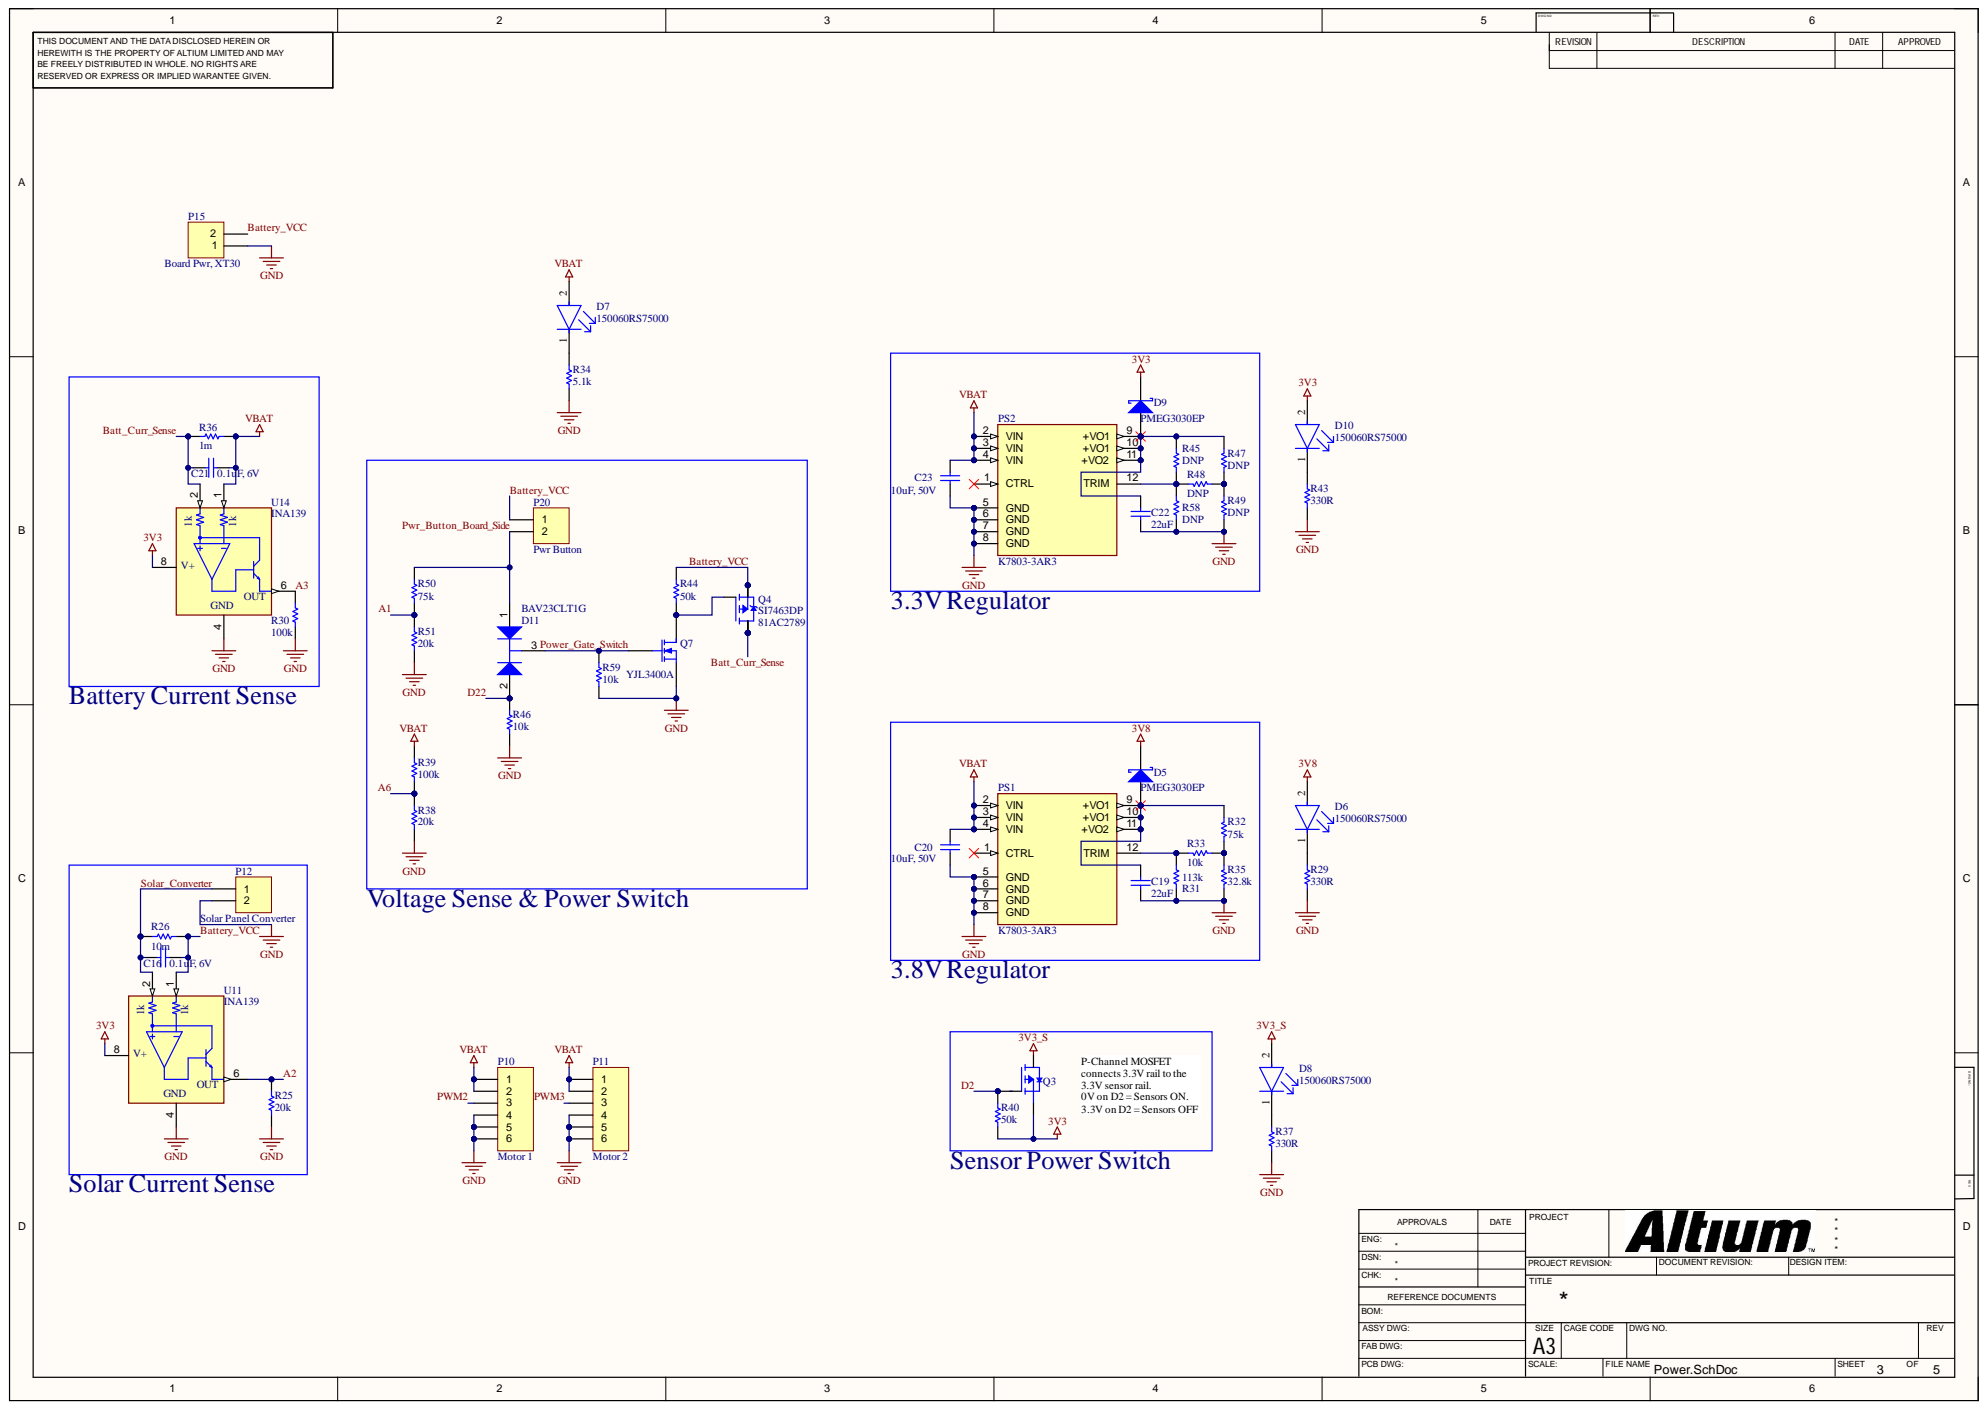
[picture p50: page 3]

THIS DOCUM ENT AND THE DATA DISCLOS ED HEREIN OR HERE WITH IS THE PROP ERT Y OF A LTIUM LIMIT ED AND M AY B E FRE E LY DIS TRIBUT ED IN WHOL E. NO RIGHT ARE RE S ERV ED OR E X PRE S S OR IM P LIED W ARANT E E GIV EN. | VBAT 150060RS750 00 | R E V I I ON | D E C R I PT I ON | D AT E | A P P R OVE D

nel MO
nects 3.3V rail to the

A P PROV A L S | DAT E | PROJECT | ****

ENG:
** DSN:

CHK :

PROJECT RE VISION: | DOCUM ENT RE VISION: | DE SIGN IT E M :

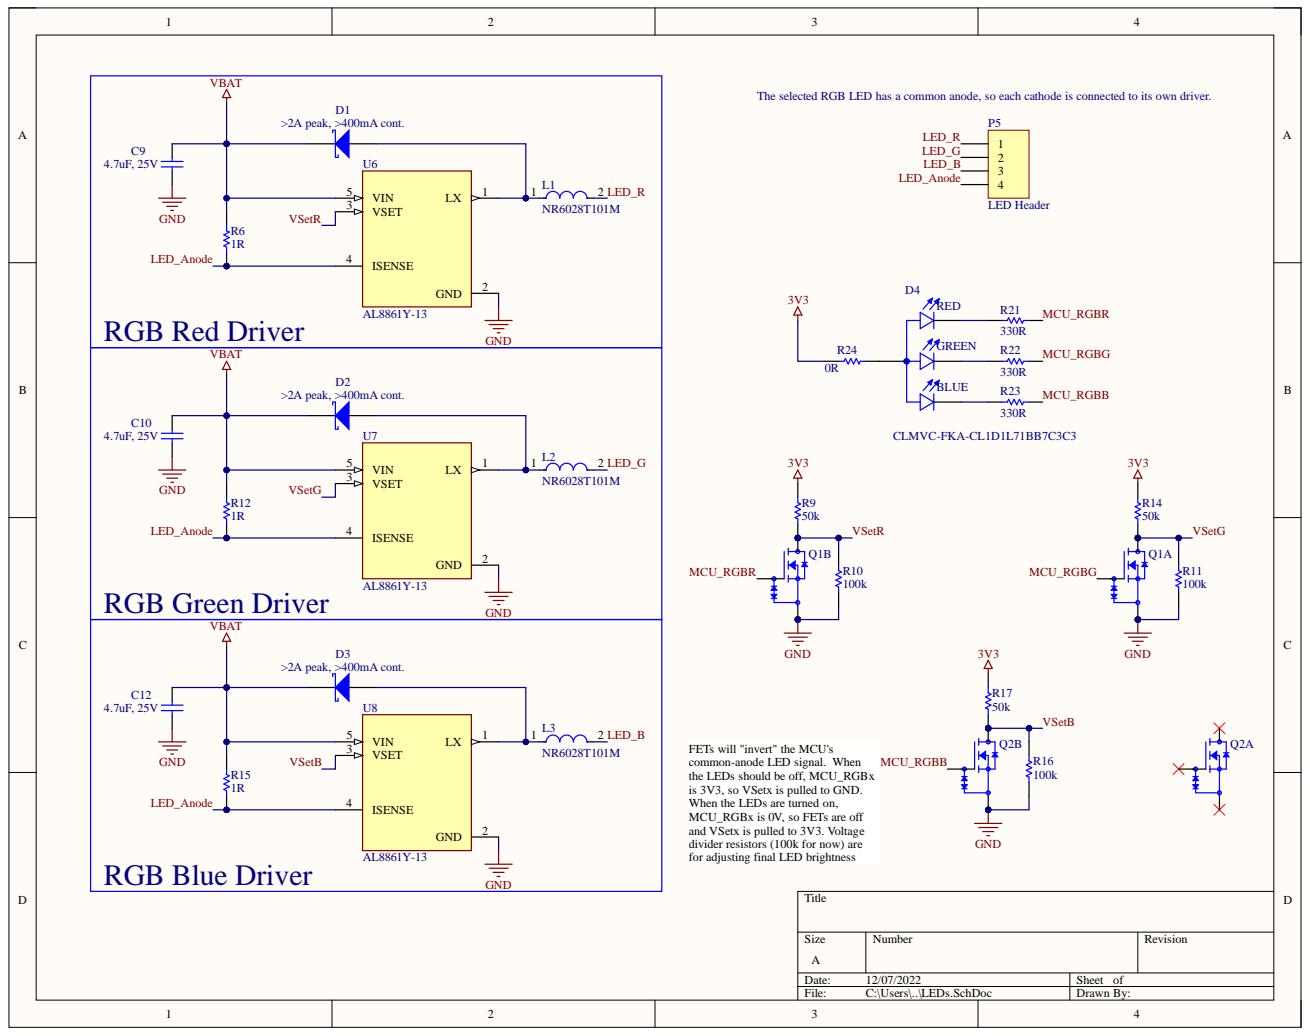
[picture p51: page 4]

The selected RGB LED has a common anode, so each cathode is connected to its own driver.

FETs will "invert" the MCU's
common-anode LED signal. When
the LEDs should be off, MCU_RGBx
is 3V3, so VSetx is pulled to GND.
When the LEDs are turned on,
MCU_RGBx is 0V, so FETs are off
and VSetx is pulled to 3V3. Voltage
divider resistors (100k for now) are
for adjusting final LED brightness

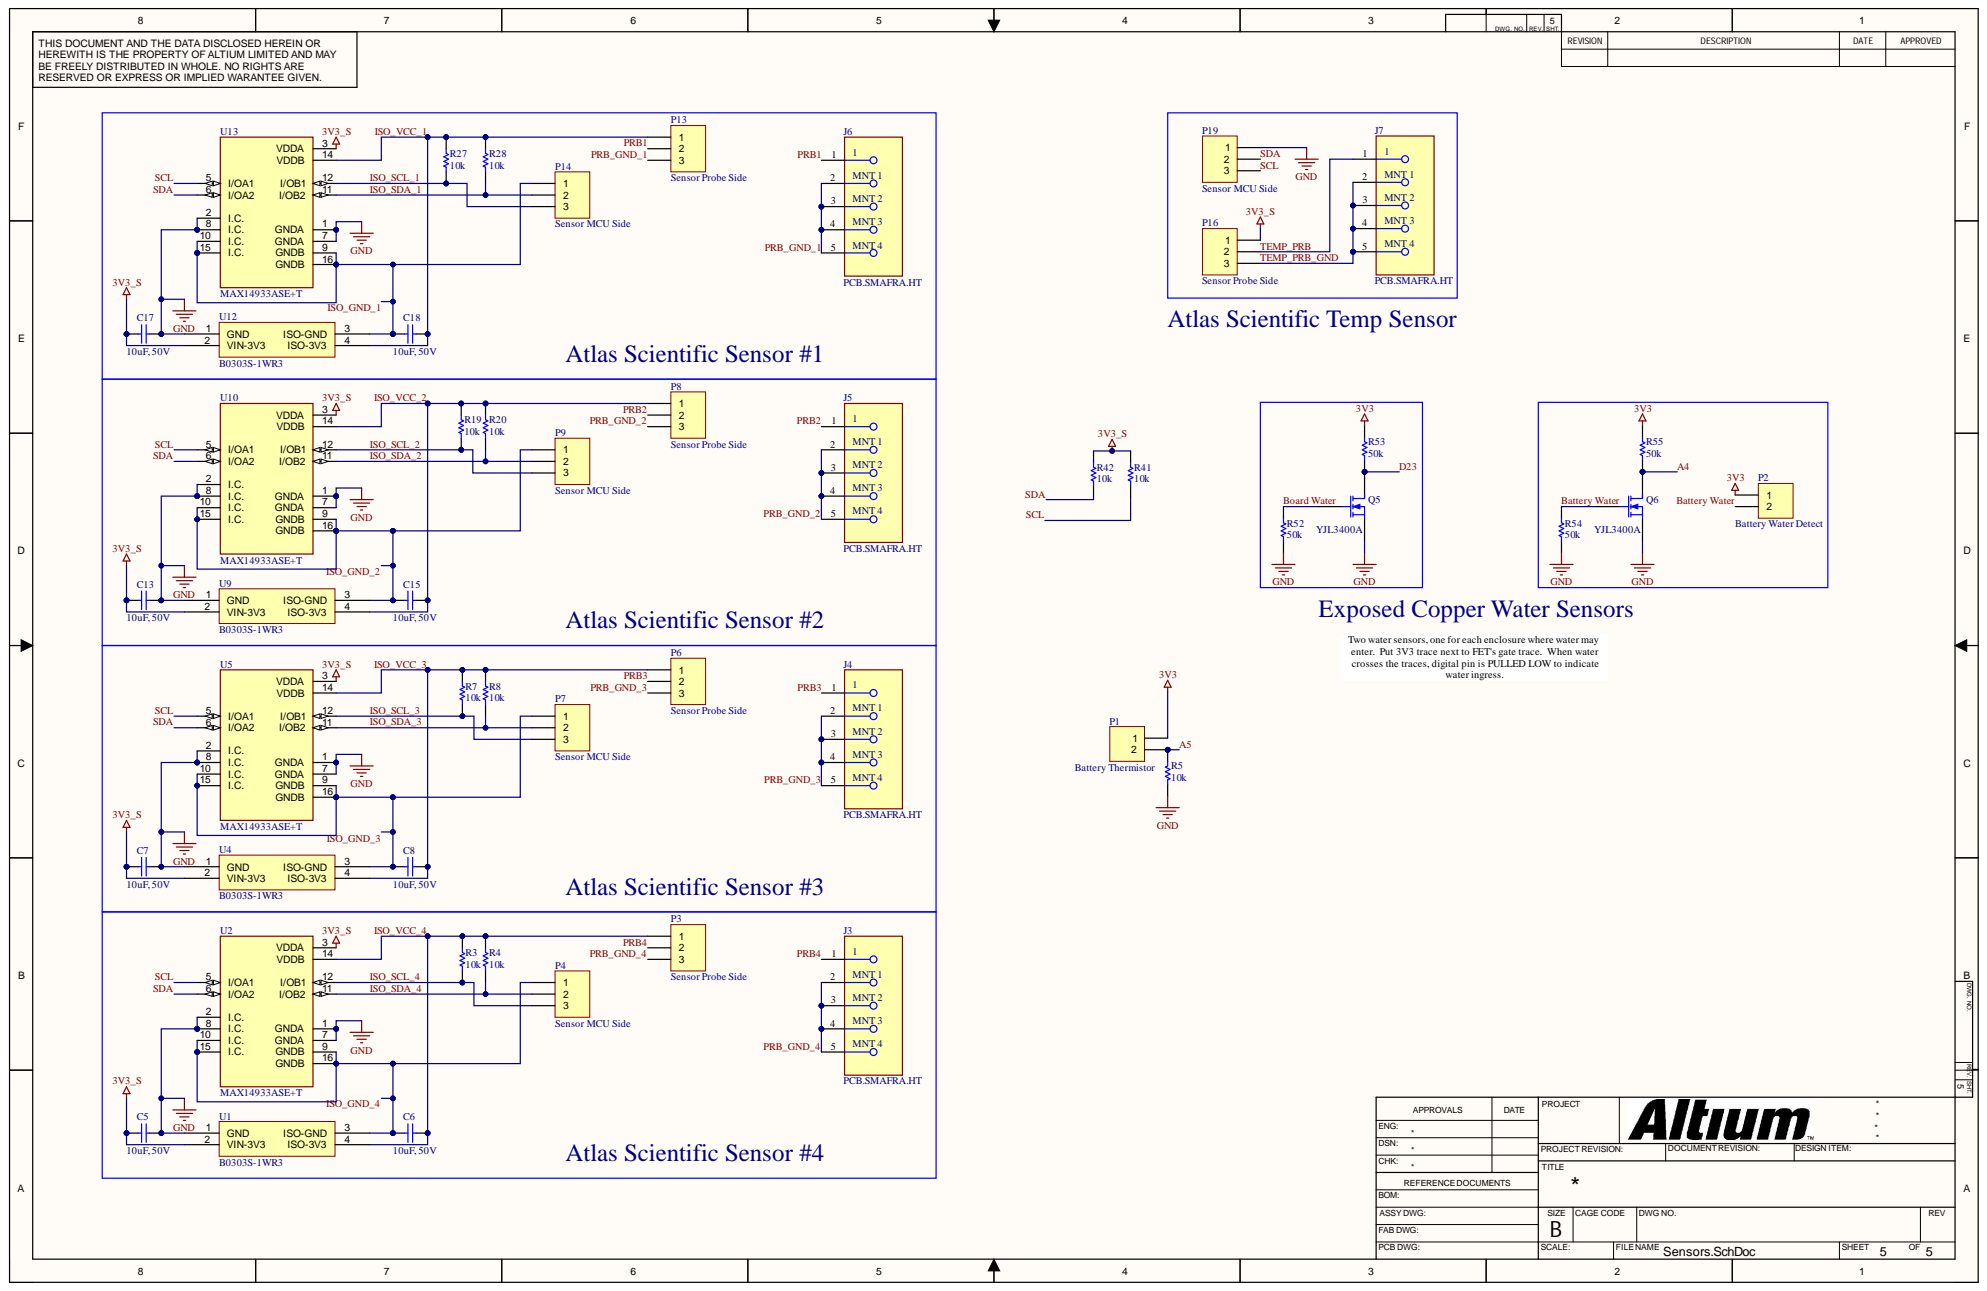
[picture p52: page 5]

T H I S D O C UME N T A N D T H E D AT A D I S C L O S E D H E R E I N O R H E R EWI T H I S T H E P R O P E R T Y O F A LT I UM L IMI T E D A N D MAY B E F R E E LY D I S T R I B U T E D I N WH O L E . N O R I G H T S A R E R E S E R V E D O R E X P R E S S O R IMP L I E D WA R A N T E E G I V E N . | | RE V I S I O N | DE SCRI PT I O N | DAT E | A P PROV E D

1 0 | | 7
1 5 | I . C . G N D B G N D B | 9 | G N D

REV. SHT. DWG. NO.

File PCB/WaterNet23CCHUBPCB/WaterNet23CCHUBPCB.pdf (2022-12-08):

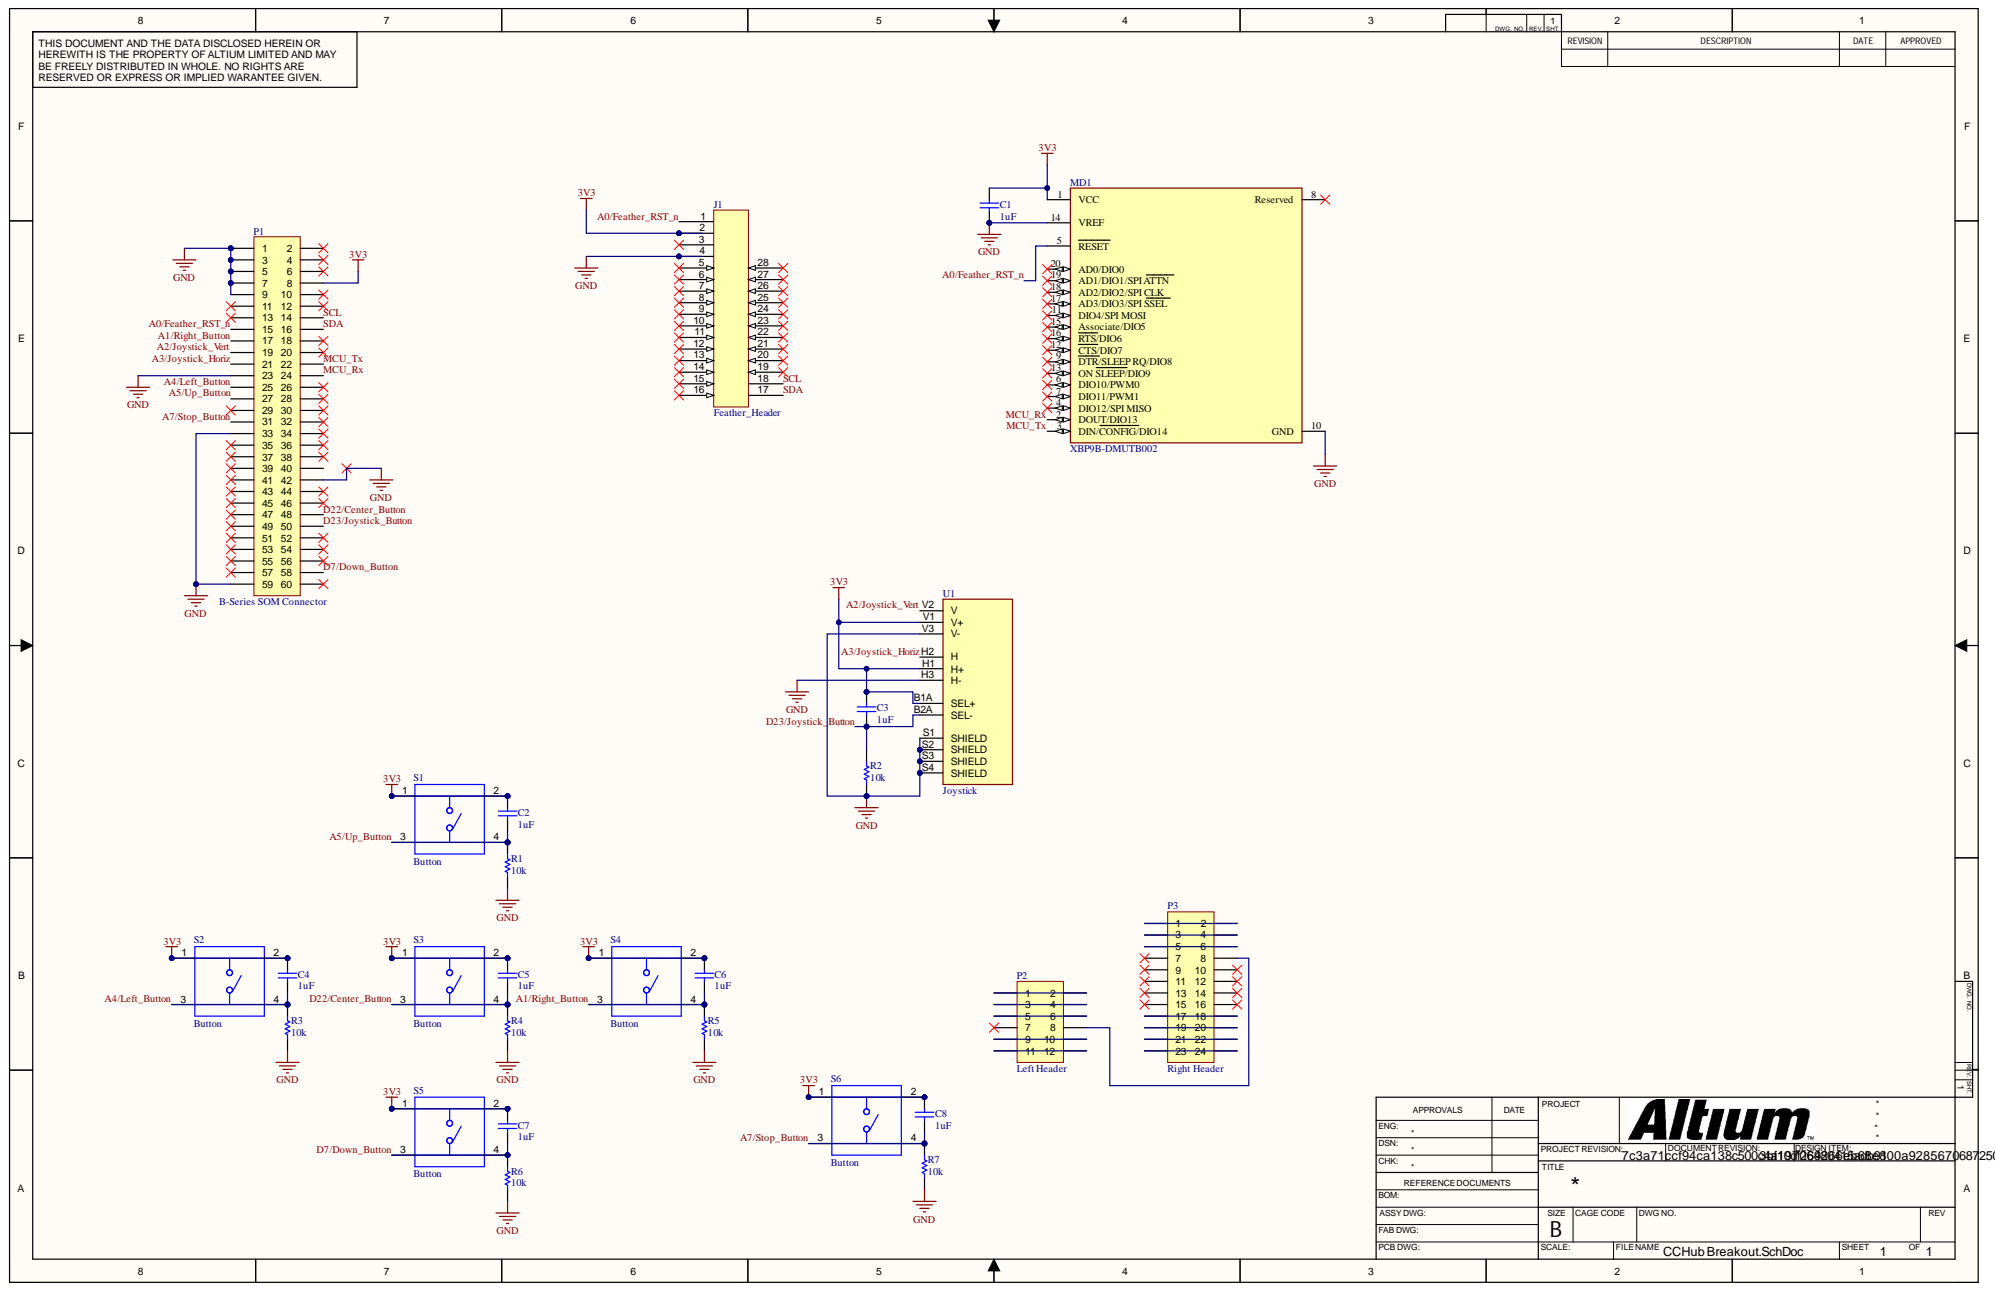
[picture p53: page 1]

8 | 7 | 6 | 5 | 4 | 3 | DWG. NO. | REV. | 1 SHT. | 2 | 1

THIS DOCUMENT AND THE DATA DISCLOSED HEREIN OR HEREWITH IS THE PROPERTY OF ALTIUM LIMITED AND MAY BE FREELY DISTRIBUTED IN WHOLE. NO RIGHTS ARE RESERVED OR EXPRESS OR IMPLIED WARANTEE GIVEN. | 3V3 | REVISION | DESCRIPTION | DATE | APPROVED

A3/Joystick_Horiz | H H2

SEL+ B1A

REV. SHT. DWG. NO.

DATE | PROJECT | * * APPROVALS * *

ENG: *

DSN: *

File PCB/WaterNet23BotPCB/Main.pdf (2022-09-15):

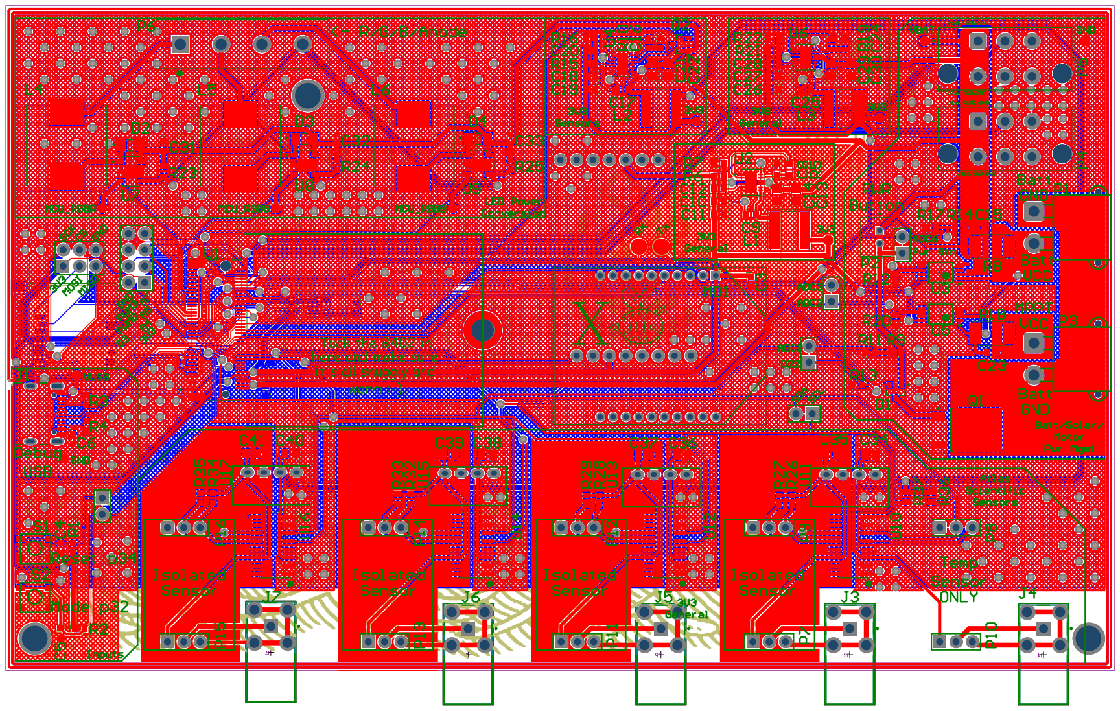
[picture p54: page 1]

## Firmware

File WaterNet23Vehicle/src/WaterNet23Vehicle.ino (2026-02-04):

/*
 * Project WaterNet23PreAlpha
 * Description: Initial code for B404 with GPS and serial communications
 * Date: 3/18/2022
 */
//////////////////////////////////////////////////////////////
//                Main Software Architecture                //
//                                                          //
//    Read these functions to understand code flow          //
//    -- setup(): Initializes hardware, timers, counters    //
//    -- loop(): Main body, contiunously executes           //
//    -- processCommand(): command dictionary from comms    //
//                                                          //
//  Timers: read these to understand asynchronous activity  //
//                                                          //
//////////////////////////////////////////////////////////////

#include "application.h"                    //Needed for I2C to GPS
#define ARDUINO 0
#include "SparkFun_u-blox_GNSS_Arduino_Library.h"
#include <Adafruit_Sensor.h>
#define X_AXIS_ACCELERATION 0
//#include "SparkFun_Ublox_Arduino_Library.h" //http://librarymanager/All#SparkFun_Ublox_GPS
//#include <MicroNMEA.h>                      //http://librarymanager/All#MicroNMEA
#include "SdFat.h"
#include "sdios.h"
#undef min
#undef max
#include <vector>
#include <stdarg.h>
#include "CompassEKF.h"
#include "CompassBase.h"
#include "GPSBase.h"
#include "LIS3MDLCompass.h"
#include "LSM303Compass.h"
#include "NeoM8UGPS.h"
#include "VehicleSimulator.h"
#include "CommandQueue.h"

#define COMPASS_TYPE_LSM303     0           //Value for COMPASS_TYPE to indicate LSM303DLHC    
#define COMPASS_TYPE_LIS3MDL    1           //Value for COMPASS_TYPE to indicate LIS3MDL
#define COMPASS_TYPE_AUTO       2           //Value for COMPASS_TYPE to auto-detect compass

#define COMPASS_TYPE            COMPASS_TYPE_AUTO           //0 = LSM303DLHC, 1 = LIS3MDL


SYSTEM_MODE(SEMI_AUTOMATIC);
SYSTEM_THREAD(ENABLED);

///////////////////////
// BLE Configuration //
///////////////////////

const char* WaterNetService = "b4206910-dc4b-5743-c8b1-92d0e75182b0"; //Main BLE Service
const char* rxUuid          = "b4206912-dc4b-5743-c8b1-92d0e75182b0"; //GPS Latitude Service
const char* txUuid          = "b4206913-dc4b-5743-c8b1-92d0e75182b0"; //GPS Longitude Service
const char* offldUuid       = "b4206914-dc4b-5743-c8b1-92d0e75182b0"; //GPS Longitude Service

BleCharacteristic txCharacteristic("tx", BleCharacteristicProperty::NOTIFY, txUuid, WaterNetService);
BleCharacteristic rxCharacteristic("rx", BleCharacteristicProperty::WRITE_WO_RSP, rxUuid, WaterNetService, BLEDataReceived, NULL);
BleCharacteristic offloadCharacteristic("off", BleCharacteristicProperty::NOTIFY, offldUuid, WaterNetService);

#ifdef BLE_DEBUG_ENABLED
    const char* bledbgUuid      = "b4206915-dc4b-5743-c8b1-92d0e75182b0"; //BLE Debug Console characteristic
    BleCharacteristic bledbgCharacteristic("dbg", BleCharacteristicProperty::NOTIFY, bledbgUuid, WaterNetService);
#endif

BleAdvertisingData advData;                         //Advertising data

uint8_t BLECustomData[CUSTOM_DATA_LEN];             //Byte array for custom data transmitted in the BLE advertising packet. Can contain up to 31 bytes in an advertisement

////////////////////
// Timer Objects //
///////////////////

Timer watchdog(WATCHDOG_PD, wdogHandler);           //Create timer for watchdog, which checks if certain methods of communication are available
Timer ledTimer(300,LEDHandler);                     //Create timer for LED, which updates the color of the LED based on what communication/hardware modes are available
Timer motionTimer(250, motionHandler);             //Create timer for motor watchdog, which cuts off motors if messages from CC have not been received recently enough
Timer motorHandler(MTR_RAMP_TIME,updateMotors);
Timer statusPD(STATUS_PD,StatusHandler);            //Create timer for status, which calculates the status values that will be transmitted to CC and sets a flag for transmitting out the status


//////////////////////////////
// Logging Global Variables //
//////////////////////////////

CommandQueue commandQueue;                      //Command queue for incoming commands from various sources. Helps with thread-safety and asynchronous command processing
CommandQueue debugQueue;                        //Command queue for debug messages to be logged to the uSD card. Helps with thread-safety and asynchronous command processing


VehicleSimulator* vehicleSim = nullptr;         //Pointer to the vehicle simulator object, if enabled
CompassBase* compass = nullptr;                 //Unified compass pointer using abstract base class
GPSBase* gps = nullptr;                         //Unified gps pointer using abstract base class

LEDStatus status;                               //LED Control object

//////////////////////////////
// Logging Global Variables //
//////////////////////////////

// uSD controller class
SdFat sd((SPIClass*)&SPI);                      //SD card object, initialized on SPI for the Beta/Alpha PCB, SPI1 on the Bsom breakout board

// Filename strings
char filename[MAX_FILENAME_LEN];                //Filename for the file holding sensor data
char logFileName[MAX_FILENAME_LEN];        //Filename for the file holding log messages
char simFilename[MAX_FILENAME_LEN];             //Filename for the simulation data log file
char autFilename[MAX_FILENAME_LEN];             //Filename for the autonomous navigation data log file

// Data log files
File dataFile;                                  //File for the sensor data
File logFile;                                   //File for messages logged by the program
File simLogFile;                                //File for simulation data logging
File autLogFile;                                //File for autonomous navigation data logging
File logDir;                                    //File directory 

bool SDAvail;    
bool logSensors = true; 
bool logMessages = true;                                 //Flags for sensor timing/enables
bool statusTableEnabled = true;                                                //Flag to control status table printing

SerialLogHandler logHandler(LOG_LEVEL_INFO);    //Log Configuration


////////////////////////////////////
// Motor Control Global Variables //
////////////////////////////////////

// Instances of the servo class for controlling the ESCs
Servo ESCL;                                                             //Object for servo esc of left motor 
Servo ESCR;                                                             //Object for servo esc of right motor

uint8_t leftMotorSpeed, leftMotorSpeedSetpoint;                         //Global for the left motor speed and left motor target speed
uint8_t rightMotorSpeed, rightMotorSpeedSetpoint;                       //Global for the right motor speed and right motor target speed

bool stopActive = false;                                                //Flag to indicate that the CChub has had a stop hit
uint32_t lastMotorCommandTime;                                          //Timers for when the last motor control command was received


////////////////////////////////////
//   Navigation Global Variables  //
////////////////////////////////////

bool usingVehicleSim = false;                                           //Flag to indicate that the vehicle simulator is being used instead of real GPS/compass
float latitude, longitude;                                              //Globals to hold the latitude and longitude read in from the GPS
float compassHeading; 
float travelHeading, headingDelta;                                      //Compassheading is the calibrated compass reading relative to north, travel heading is the heading between current point and target point
float targetLat, targetLon;                                             //Globals to hold the latitude and longitude sent from the CC for where the bot should target
float travelDistance;                                                   //Global to hold the distance between the current latitude and longitude and the target latitude and longitude
bool telemetryAvail = false;                                            //Boolean global to check if the compass and GPS are available
bool waypointArrived = false;                                           //Flag to indicate that the waypoint has been reached
uint16_t waypointIndex = 0;                                             //Index of the waypoint this bot is currently targeting

double varCompassHead;
int compOffset = COMP_OFFSET;                                           //Offset for the compass calibration. Degrees off north to add to the compass reading to calibrate it to true north
bool doCompassCal = false;                                              //Flag to indicate that the compass calibration has been requested
bool GPSAvail = false;                                                  //Flag to indicate that the GPS is available
bool CompassAvail = false;                                              //Flag to indicate that the compass is available

uint16_t motorTare = 100;                                               //Tare value for the motors, used to calibrate the ESCs when one motor is faster than the other

uint32_t lastTelemTime = 0;
uint32_t lastCalibrationTime = 0;                                       //Timer for when the last compass calibration occurred 
uint32_t lastAutonomousLogTime = 0;                                     //Timer for when the last autonomous navigation data was logged

uint8_t driveMode = DRIVE_MODE_MANUAL;                                  //Global mode for drive mode, 0 = manual remote control, 1 = sentry, 2 = autonomous

// EKF variables for improved compass heading
CompassEKF compassEKF;                                                  //Extended Kalman Filter for compass heading fusion
float filteredCompassHeading = 0.0;                                     //EKF-filtered compass heading
float lastEKFUpdateTime = 0.0;                                          //Last time EKF was updated
bool useEKF = false;                                                     //Flag to enable/disable EKF filtering

                             


////////////////////////////////////
// Communication Global Variables //
////////////////////////////////////

bool waitForConnection;                                                 //Flag used on startup until the CC acknowledges this bot
bool LTEAvail = false;                                                  //Flag to indicate that LTE is available
bool XBeeAvail = false;                                                 //Flag to indicate that XBee is available
bool BLEAvail = false;                                                  //Flag to indicate that BLE is available
uint32_t XBeeRxTime = 0, BLERxTime = 0;                                 //Timers for when the last valid Xbee and BLE message was received
bool statusReady = false;                                               //Flag to indicate that a status is ready
uint8_t requestActive = 0;                                              //Flag to indicate that a sensor request has been made from the CChub
uint16_t LTEStatusCount = LTE_MAX_STATUS;                               //Counter to determine number of LTE messages that should be sent to limit data usage
uint16_t statusFlags = 0;                                               //Global status flag
uint32_t lastStatusTime = 0;                                            //Timer for when the last status control packet was received


////////////////////////////////////
// Power System Global Variables  //
////////////////////////////////////
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

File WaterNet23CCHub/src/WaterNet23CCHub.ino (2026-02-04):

/*
 * Project WaterNet23CCHub
 * Description: Code for the Central Control hub responsible for orchestrating commands to Water Bots
 * Author: WaterNet23 - Matthew Panizza, Jake Meckley Cynthia Rios, Harrison Strag
 * Date: 9/2/22
 */


#include "application.h"
#include "SdFat.h"                              //Library for SD Card
#undef min
#undef max
#include <vector>                               //Standard C++ library for vector data type
#include <Adafruit_GFX.h>                       //Library for displaying text/shapes on standard LCDs
#include <Adafruit_SH110X.h>                    //Library to use Adafruit GFX library with this specific 128x64 OLED

// Pin Definitions

#define OLED_RESET              A0              //Pin used to reset the OLED screen on startup
#define JOYH_ADC                A2              //Horizontal Joystick
#define JOYV_ADC                A3              //Vertical Joystick ADC pin
#define JOY_BTN                 D23             //Joystick button press
#define L_DPAD                  A4              //Left DPAD button
#define R_DPAD                  A1              //Right DPAD button
#define U_DPAD                  A5              //Up DPAD button
#define D_DPAD                  D7              //Down DPAD button
#define E_DPAD                  D22             //"Enter" DPAD button
#define chipSelect              D8              //SD Card chip select pin
#define STOP_BTN                A7              //Stop button to disable all bot motors

//Program Parameters

#define DEF_FILENAME            "CCHUB"
#define BLE_OFFLD_BUF           100             //Maximum number of characters to fetch for each read from the SD card when offloading
#define SCAN_RESULT_COUNT       20              //Maximum devices to discover per scan
#define CUSTOM_DATA_LEN         8               //Number of bytes to include in the advertising packet for BLE
#define MAX_FILENAME_LEN        30              //Maximum number of characters in the filename for log files
#define MAX_ERR_BUF_SIZE        15              //Buffer size for error-return string
#define MAX_LTE_STATUSES        300             //Maximum number of statuses to send over LTE when XBee and BLE are unavailable

//Timing Control

#define XBEE_BLE_MAX_TIMEOUT    36
#define BLE_MAX_CONN_TIME       200             //20 second max time to successfully pair to bot
#define BLE_SCAN_PERIOD         1000            //Time betweeen BLE scans
#define LTE_BKP_Time            100             //Send LTE request after 10 seconds if not connected to any bot
#define LTE_CTL_PERIOD          29000           //Minimum time between sending LTE control packets periodically per bot
#define MTR_LTE_PERIOD          3000            //Minimum time between sending mtr command over LTE
#define MTR_UPDATE_TIME         250             //Frequency to send manual motor control packet in milliseconds
#define CONTROL_PUB_TIME        5000            //Number of milliseconds between sending control packets to bots
#define STOP_PUB_TIME           5000            //Time between sending stop messages when active
#define WB_MOD_UPDATE_TIME      60000           //Timeout for when status update packets will modify the class, prevents immediate overwrite when changing control variables
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

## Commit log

2022-08-24 Create data request framework
2022-08-25 Added example CSV Files
    [WaterBot08132022201054.csv, WaterBot08142022024404.csv]
2022-08-25 Added PCB Files for Water Bots
    [Main.PcbDoc, MainPCB.SchDoc, WaterNet23BotPCB.PrjPcb]
2022-08-25 Added test GND
    [MainPCB.SchDoc]
2022-08-25 No grounds. PCB is floating (in water)
    [MainPCB.SchDoc]
2022-08-26 Added motors/motor controller to block diagram
2022-08-28 Created B402 Schematic symbol and added pin definitions
    [MainPCB.SchDoc, WaterNet23BotPCB.PrjPcb, WaterNet23BotPCB.SCHLIB]
2022-08-29 Added SD Card and buttons
    [B402.SCHLIB, GCT_MEM2051-00-195-00-A.PcbLib, MEM2051-00-195-00-A.SchLib, MainPCB.SchDoc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]
2022-08-30 Finished status update framework
2022-08-30 Finished all sheets except power and motors
    [AL8861Y-13.PcbLib, AL8861Y-13.SchLib, DW0016A.stp, GCT_USB4105-GF-A.PcbLib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]
2022-08-30 Finished all sheets except for power and motors
2022-09-01 Bom Bom BOMMMMMM!
    [MainPCB.SchDoc, Sensors.SchDoc, UserInputs.SchDoc]
2022-09-02 More power stuff added to schematic
    [MainPCB.SchDoc, Power.SchDoc, SnapEDApcb.PcbLib, SnapEDAsch.SchLib]
2022-09-02 Added more power stuff to schematic
2022-09-03 Big ol' PCB Layout
    [1586039-6.SchLib, 1586039-6.stp, 21992304.SchLib, 2512 Resistor.PcbLib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]
2022-09-05 Started voltage regulation schematics (no values added yet)
    [DFN12LD 3x4.PcbLib, DFN12_4X3_INR.step, ISL85003AFRZ.SchLib, MainPCB.SchDoc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]
2022-09-07 Everything But The Tracks (TM)
    [Custom_Footprints.PcbLib, LEDs.SchDoc, Main.PcbDoc, MainPCB.SchDoc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]
2022-09-07 USB Can have a little high-speed routing... As a treat
    [AL8861Y-13.PcbLib, AL8861Y-13.SchLib, Main.PcbDoc, MainPCB.SchDoc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]
2022-09-08 Everything But The Vias (TM)
    [2512 Resistor.PcbLib, 350761-4.PcbLib, 6-440054-2.PcbLib, AAL8861Y-13.PcbLib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]
2022-09-08 Replaced I2C isolator in schematic
    [MAX14933ASE+T.STEP, MAX14933ASE+T.SchLib, SOIC127P600X175-16N.PcbLib, Sensors.SchDoc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]
2022-09-09 Final draft before PCB Review
    [1-2_Header.stp, 1-3_Header.STEP, 1-3_Socket.STEP, 2-3_Header.STEP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]
2022-09-10 Added STEP file of board
2022-09-12 Added manual motor control to bots
2022-09-13 Debugging manual motor control
2022-09-13 Fixed manual motor control, updated block diagram.
2022-09-13 Changed PWM0 -> PWM2 on motor. Added silkscreen descriptions
    [Custom_Footprints.PcbLib, MainPCB.SchDoc, Power.SchDoc, SOIC127P600X175-16N.PcbLib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]
2022-09-13 Fixed XBee Code, tested motor control
    [Custom_Footprints.PcbLib, MainPCB.SchDoc, Power.SchDoc, SOIC127P600X175-16N.PcbLib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]
2022-09-13 Added U-Blox GPS and lots of silkscreen
    [7-Pin Socket.stp, 8-Pin Socket.stp, Custom_Footprints.PcbLib, MainPCB.SchDoc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]
2022-09-15 Gerber files added and debounce resistor changed
    [Main.GBL, Main.GBO, Main.GBP, Main.GBS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]
2022-09-15 Changed the debounce resistor
    [UserInputs.SchDoc, WaterNet23BotPCB.PrjPcb]
2022-09-22 Added command for sensor request
2022-09-29 Small edits to bot PCB, created schematic and board layout for CCHUB
    [12x2.STEP, 2x30.step, 6x2.STEP, CCHUB_Footprints.PcbLib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]
2022-09-29 Added code for sensor power enable
2022-09-29 Fix code for Pi to CCHub sensor status update
2022-09-29 Measured part locations
    [CCHUB_Footprints.PcbLib, Main.PcbDoc]
2022-09-30 Board routed, still need stitching vias and silkscreen edits
    [Main.PcbDoc, WaterNet23CCHUBPCB.PrjPcb]
2022-09-30 Added stitching vias and silkscreen
    [Main.PcbDoc]
2022-10-05 Changed positioning of headers because they were off
    [Main.PcbDoc]
2022-10-11 Added power system monitoring and motor cutoff
2022-10-17 Added LED changes and fixed communication lines being swapped
    [CCHub Breakout.SchDoc, CLMVC-FKA-CL1D1L71BB7C3C3--3DModel-STEP-56544.STEP, Custom_Footprints.PcbLib, JST_SM04B-SRSS-TB(LF)(SN).PcbLib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]
2022-10-17 More work on power input, implemented & verified quiic connector
    [8-SOIC.step, BetaPCB.PcbDoc, Custom_Footprints.PcbLib, JST_SM04B-SRSS-TB(LF)(SN).PcbLib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]
2022-10-19 Updated power schematics and BOM
    [CONV_K7803-3AR3.PcbLib, K7803-3AR3.SchLib, K78xx-3AR3.stp, LEDs.SchDoc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]
2022-10-19 Schematic completed, board rules and footprints added but haven't started with layout
    [0603 Resistor.step, AAL8861Y-13.PcbLib, Custom_Footprints.PcbLib, LEDs.SchDoc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]
2022-10-20 Getting dunked on by non-standard MOSFET pin layouts
    [Power.SchDoc, Sensors.SchDoc]
2022-10-24 Started work on component placement, fixed a few bugs with power connections
    [Custom_Footprints.PcbLib, Power.SchDoc]
2022-10-25 Beta PCB is certifiably laid out
    [LEDs.SchDoc, MainPCB.SchDoc, Power.SchDoc, UserInputs.SchDoc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]
2022-10-26 Everything laid out on the board except traces
    [WaterNet23BotPCB.PrjPcb]
2022-10-26 Filling out ground planes and begun routing LED circuits
    [LEDs.SchDoc, MainPCB.SchDoc, Power.SchDoc, Sensors.SchDoc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]
2022-10-27 Finished compass calibration. Added heading delta
2022-10-27 Lotsa Extra Routing, Inc.
    [ANTC1608X90N.PcbLib, CAPC2012X145N.PcbLib, Custom_Footprints.PcbLib, MainPCB.SchDoc]
2022-10-27 Keep Chugging on tha Routing
    [MainPCB.SchDoc, Power.SchDoc]
2022-10-27 Added motor calculation based on delta
2022-10-28 Finished all routing and silkscreen/mask errors - Zero DRC violations
    [2512 Resistor.PcbLib, 350761-4.PcbLib, AAL8861Y-13.PcbLib, ANTC1608X90N.PcbLib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]
2022-10-28 Replaced AO4616 with separate N & P-Ch FETS
    [Power.SchDoc, SI7463DP.STEP, SIR165DP.PcbLib, SIR165DP.SchLib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]
2022-10-28 Added Gerbers and checked everything over again
    [1-2_Header.stp, 1-3_Header.STEP, 1-3_Socket.STEP, 12x2.STEP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]
2022-11-01 Fixed/tested autonomous motor values
2022-11-04 Fixed Pi rx serial, fixed offloading, fix motor
2022-11-10 Fix sensor loop halt bug, menu improvements
2022-11-11 Added stop button, DO sensor, pwr button input
2022-11-25 Fixed motor ramping algorithm
2022-11-29 Moved motor handler to interrupt
2022-12-08 Fixed Beta PCB design errors
    [BetaPCB.GBL, BetaPCB.GBO, BetaPCB.GBP, BetaPCB.GBS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]
2022-12-08 Fixed LCD reset error
    [CCHUB_Footprints.PcbLib, Main.GBL, Main.GBO, Main.GBP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]
2022-12-08 Fixed silkscreen on reset pin
    [Main.PcbDoc]
2022-12-08 Added 3D models for CCHUB Case
    [CCHUB Bottom Case.stl, CCHUB Button.stl]
2025-04-12 Rename WaterNet23PreAlpha folder to WaterNet23Vehicle
    [WaterBot08132022201054.csv, WaterBot08142022024404.csv]
2025-04-26 Remove old LISMDL quadrant-based calibration. Add basic offset calibration for compass with measurement via cmp command
2025-04-26 Add Compass Heading statistic and calibration mode
2025-07-22 Break out commands into helper functions. Add compass abstraction for allowing multiple compass types. Add EKF for filtering compass data. Add Serial handling for local command receiving. Add printou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
2025-07-24 Have vehicle capture current latitude/longitude as the new target when switching to Sentry mode. Add drive mode macros. Add abstraction for printing to debug log on SD card.
2025-07-24 Implement Command Queue to handle multi-mode communication in a thread-safe manner. Remove SD card logging from command reception callbacks to fix panic.
2025-07-24 Add feature to perform action based on number of presses of the power button
2025-07-26 Finish compass calibration sequence. Fix EEPROM storage of calibration value. Add LED pattern to indicate calibration happened.
2025-07-29 Update kinematics simulation to emulate compass based on motor speed differential. Add simulation scenario for diagonal movement
2025-07-29 Create queue for debug messages for functions operating in threads. Should fix suspected crash caused by uSD card SPI.
2025-08-30 Add dynamic publish rate control to CCHub. Add target heading and current motor speeds to status update packet. Break out CCHub command processor into helper functions like vehicles. Code refactoring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
2025-10-02 Add motor tare functionality
